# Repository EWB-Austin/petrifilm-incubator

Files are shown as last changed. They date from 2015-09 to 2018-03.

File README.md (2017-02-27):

# The Armadillo v1.0, a Low-cost, Portable, Petrifilm Incubator

The Armadillo v1.0 is a low-cost, portable Petrifilm(TM) Incubator for doing in-country bacterial analysis of water quality for Engineers Without Borders invented and engineered by the Instrumentation Group of [Great Austin Chapter](https://ewbgreateraustin.org/) of [EWB-USA](http://www.ewb-usa.org/).

Watch a 3-minute introductory [video](https://www.youtube.com/watch?v=0SzoYT8wLo0)!

The Armadillo won [1st place](https://ewbgreateraustin.org/2016/11/01/test/) in in the 2016 SCSE Regional Conference in Atlanta poster session contest.
As we like to say, "we beat NASA", with our [poster](https://github.com/EWB-Austin/petrifilm-incubator/blob/master/doc/EWBconferenceposterIncubator_handout_comp.pdf):

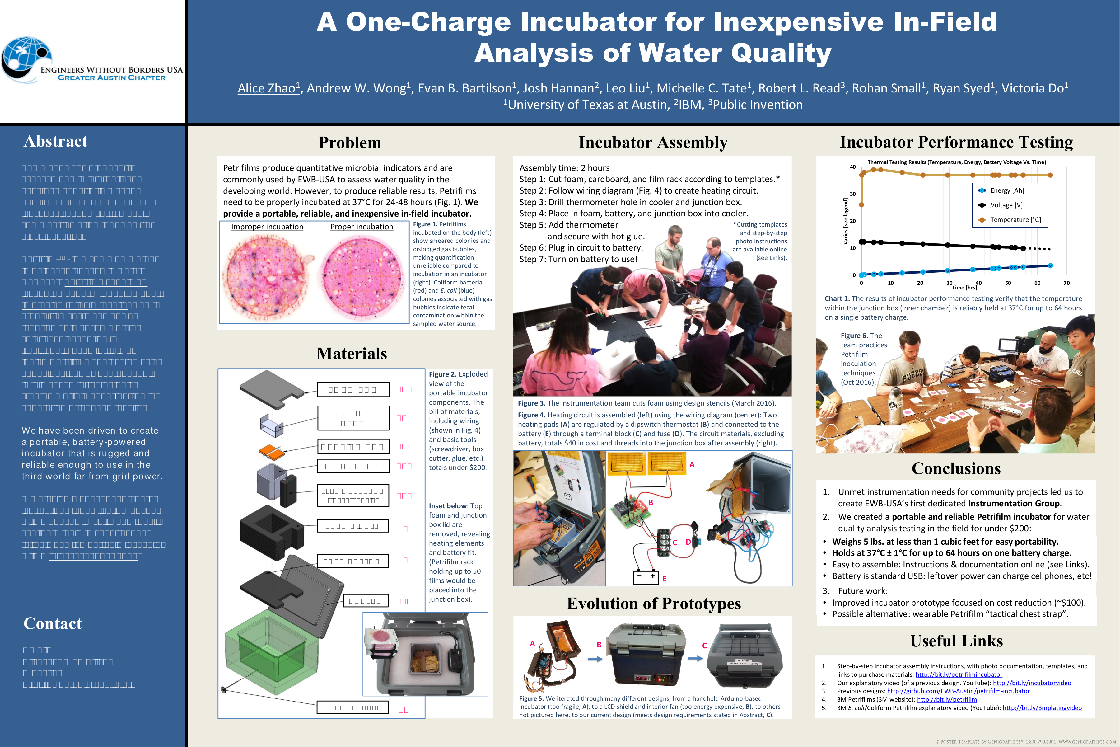
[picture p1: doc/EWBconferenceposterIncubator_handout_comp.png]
poster
.

## Start Here: Documentation

We have a press release in progress which is not yet published.

Our [instructable](http://www.instructables.com/id/Portable-Petrifilm-Incubator-for-Inexpensive-In-Fi/)
gives step-by-step instructions for the construction of the Armadillo for about $160.

For those who prefer printable and sharable PDF, we have prepared a [construction manual](https://github.com/EWB-Austin/petrifilm-incubator/blob/master/doc/ConstructionManual.pdf).

Because the use of the Armadillo requires inoculating Petrifilms, we have prepared an
[inoculation manual](https://github.com/EWB-Austin/petrifilm-incubator/blob/master/doc/PetrifilmInoculation.pdf).

In the [experiments](https://github.com/EWB-Austin/petrifilm-incubator/tree/master/experiments) directory
you will find data from our battery-lifetime experiments.

## Status of the Project

We are:
* Preparing an academic paper with a plan to submit it to [Journal of Humanitarian Engineering](https://www.ewb.org.au/jhe/index.php/jhe).
* Planning some small improvements to create the Armadillo v2.0, such as the inclusion of a screwdriver and
a user manual in the Armadillo itself.
* Promoting the use and construction of the Aramadillo within EWB chapters.

## How You Can Help

We need someone to build an Armadillo!  Although we hope our published materials are self-sufficient,
we are happy to provide personal assistance and help in building your own Armadillo. We want to make
sure that our instruction materials are high-quality.

Please email: <a href="mailto: instrumentationmembers@ewbgreateraustin.org"> instrumentationmembers@ewbgreateraustin.org</a>  or visit our [chapter website](https://ewbgreateraustin.org/) to contact us.

## Older Documents

Our older README is [archived](https://github.com/EWB-Austin/petrifilm-incubator/2016-README.md).

## Contact

[Great Austin Chapter](https://ewbgreateraustin.org/) of [EWB-USA](http://www.ewb-usa.org/).
<a href="mailto: instrumentationmembers@ewbgreateraustin.org"> instrumentationmembers@ewbgreateraustin.org</a>

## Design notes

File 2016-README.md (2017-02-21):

# petrifilm-incubator
A low-cost, portable Petrifilm(TM) Incubator for doing in-country bacterial analysis of water quality for EWB.

Watch a 3-minute introductory [video](https://www.youtube.com/watch?v=0SzoYT8wLo0)!

# Older Materails (These are now mostly obsolete.)

## Problem

Engineers Without Borders does wonderful work providing better-quality water to under-developed communities. Essential
to this is water quality analysis. The 3M Petrifilm(TM) is a widely used way of assessing bacteria load. It requires that
inocultated films be incubated at precise temperatures. Generally, EWB works in communities that have no electrical grid.
The problem then is to reliably incubate the Petrifilm with battery power.

EWB has discoverd that by doing this locally rather than sending the films to a lab, we build trust with the local communities.

An EWB Austin member, Anjan Contractor, led the creation of an initial prototype.  However, it is fragile and undocumented.
This project intends to build a robust, cheap, easy-to-make, easy-to-use, well-documented extension of this prototype.

incubatordiagram

## Commercial Solutions

<p> Eric found the following potential commercial solutions:
[Compact Incubator](http://nelsonjameson.com/Compact-Incubator-p1298.html)  This is $94. We are trying to determine if this can be used with a 12 Volt battery. We may buy one for experimentation.
</p>

<p>
[Bigger Incubators](http://www.darwinchambers.com/Portable-Incubators.html)  These don't have prices listed.
</p>

## Notes from November 14th

After purchasing Compact Incubator mentioned above, we find it completely inadequate to our purposes.

We have, however, made signifcant progress in the design of an improved system.

Our basic approach was to purchase a smaller cooler: [http://www.amazon.com/gp/product/B000IBWI42?psc=1&redirect=true&ref_=oh_aui_detailpage_o03_s00](http://www.amazon.com/gp/product/B000IBWI42?psc=1&redirect=true&ref_=oh_aui_detailpage_o03_s00)
and place our Arduino-based system inside it, with the battery on the outside.

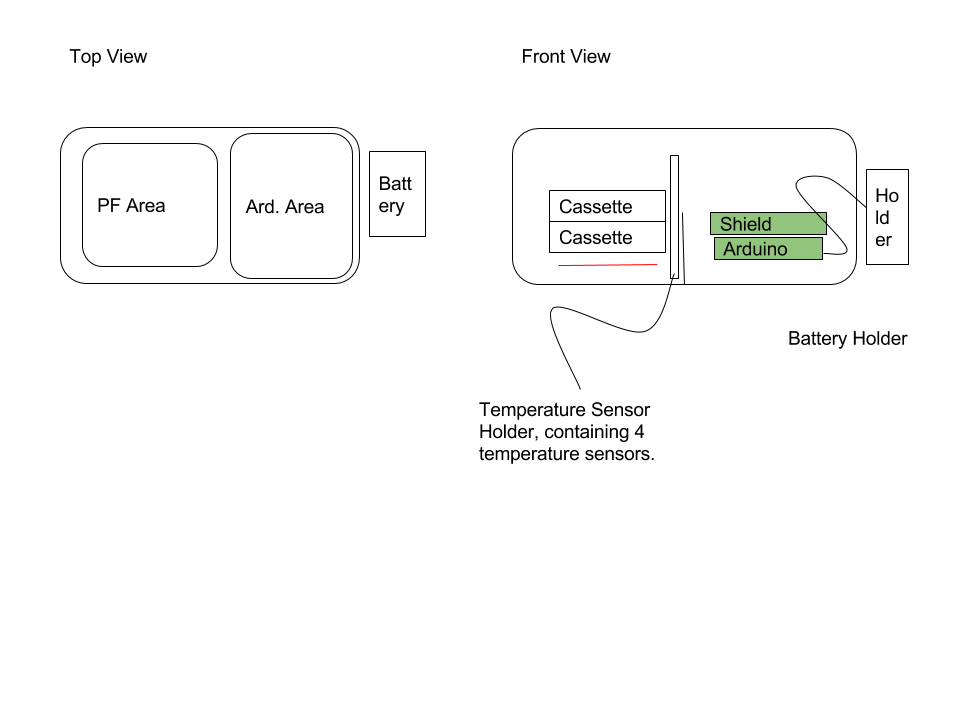
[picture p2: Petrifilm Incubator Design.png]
Image of Yaktocat


## Research Notes

(Thanks to Alice Zhao.)

1-5.
An evaluation of 5 different coliform detection techniques used on-site, including the 3 I talked about in Monday's presentation (Petrifilm, waterworks EZ(which they refer to as just MUG), lacotte multi-tube). They address some of the same issues I brought up, among other useful information.
http://www.ewb-usa.org/files/EWB-USA-TP-104-Fecal-Coliform-Contamination-of-Drinking-Water-an-Evaluation-of-World-Field-Techniques-revc.pdf

6. A 6th method of coliform detection similar to petrifilm but that can be stored at room temperature:
http://www.ewb-usa.org/files/2015/05/AssessmentWaterTestingTechniquesEColi.pdf
Product: http://www.emdmillipore.com/US/en/product/Coli-Count%E2%84%A2-Sampler,MM_NF-MC0010025?bd=1
evaluation of product robustness (for food. full disclaimer I have not read this paper)

7. Colilert is apparently also used by some EWB groups. I thought it was way too expensive when I was initially researching but I may have been wrong. I'll have to do more research on this.

7. A nice blog post of an EWB trip. They used actual petri dishes plates. According to Jen, this is what they use in her workforce when testing for coliform. I don't think this is a top candidate method for us but I like the blog and think we should do something similar for our trip.
http://www.ewbny.org/june_trip_update_part_2_quality_control

8. You asked about "presumative" coliform test and I don't feel like I gave a clear answer. 
Page 2 of this lab manual has a much better explanation.

9. An easy-to-read presentation on water testing in developing countries. Not as informative as it looks at first glance to me, but worth a glance. They seem to advocate using Petrifilm and the human body as an incubator. http://www.ewb-usa.org/files/2015/05/MicrobialTestingOfWater.pdf

10. I was very wrong about the lack of people using Petrifilm for water testing in developed countries. Another advocate of using Petrifilm, among some other techniques:
https://aguainroatan.wordpress.com/2015/07/31/water-testing-in-a-development-context/

Note: here is a different attempt to create that:

http://www.ewb-usa.org/files/2015/05/PortableIncubator.pdf

# Packaging Notes

I now believe it might be both possible and a good idea for us to package the temperature stand into an enclosure that contains the Arduino and the LCD shield.  This would allow the wires to be far better contained and the whole system to be neater. This will really make a big difference in the ruggedness. However, I want to get the EEPROM stuff improved so that we can test the timing.

# Update as of 12/30/2015

I've posted the results of an overnight experiment, in which we used the new EEPROM logging code to record the temperature vs time:
https://github.com/EWB-Austin/petrifilm-incubator/blob/master/TemperatureVsTime1.csv

In summary, it took a long time to warm up, and the battery died after 13 hours.  We really want to stay at 37C for 12 hours on one battery charge, so I consider this a partially successful experiment.

## The Second Prototype

This is our second prototype, based on an Arduino and an LCD shield.  It has now been potentially obsoleted by the third prototype (described below):



# Update as of 3/9/2016

Thanks largely due to the work of Evan Bartilson, we now have a third prototpye, which has currently demonstrated a battery life of 35 hours, and which we expect to acheive our goal of 48 hours.

Below are some photos of our team working and the current incubator.





# Our submission to the Rice NEWT Challenge

We have applied to the [Rice University NEWT Global Water Technology Challenge](http://ricenewt.rice.edu/competition/). We have made a short video, which we will post on April 15th after the competition.  Here is the Abstract we submitted:

## Abstract: Engineers Without Borders (EWB-USA), Austin, Petrifilm Incubator 

Providing potable water to the world requires an ability to tell when water is potable. Our experience has been that to be effective, the means of measuring bacteria and explaining it to people in the developing world must be visible, understandable, quantitative enough to support meaningful comparisons, cheap, and be done completely in the field far away from electrical power grids. Petrifilms(™) provided by 3M corporation are a standard way of accomplishing this. They must be incubated at approximately 37C for 48 hours.  This is traditionally done in the field by keeping the films in plastic bags against the skin of engineers in the field. This is uncomfortable, may not provide the correct temperature, and the films are meant to be kept flat and horizontal during incubation.

In US laboratories, commercial incubators cost hundreds or thousands of dollars. These require 110V power. We are building a portable, battery powered incubator that is rugged and reliable enough to use in the third world. This will allows trustworthy in-the-field analysis and comparison of water sources. Because the analysis is done completely locally and results in visible, comparable films, local people will appreciate and trust the result. Although in the US the growth of a single colony is considered a sign of danger, many of the communities that Engineers Without Borders works with cannot afford this level of quality and must have a quantitative tool that lets them compare water sources and water improvements solutions.

Our first prototype used an Arduino microcontroller in a hand-insulated box. Battery life was 18 hours. The operator changed the batteries before they ran out. This was shown to be effective in a remote community in Peru. However, it was fragile. In a second trip a wire broke and could not be repaired by our staff in the field, highlighting to us the importance of documentation and training.

Our second prototype is completely open-source, described at [GitHub. ](https://github.com/EWB-Austin/petrifilm-incubator) This prototype has developed into a third prototype which has held temperature at 37C for 35 hours. We have hopes of extending battery life to 48 hours with small improvements to this basic design. Our overriding goal is to produce a set of open-source instructions that allows anyone in the world to construct and reliably use the portable petrifilm incubator with modest skill and readily available tools at a total cost of $200.

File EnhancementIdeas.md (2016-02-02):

Here a number of loose enhancement ideas:

* Don't try to run two heat boxes with one Arduino.  Make separate units.
* Try to run everything on 12 volt system, but allow multiple jacks to support parallel battery capabilities.
* Put the Arduino in the heat chamber to take advantage of the waste heat.
* Keep the batteries outside.
* Use and LCD shield to provide better status.
* Provide an audio and visual alarm when the temperature is out of spec for too long.
* 

# Idea: Build the thing into the cap of a thermos bottle.

# Idea: Make it something that essentiall "wraps around" a battery pack.

# Note: I have now created a printed circuit board for this purpose.

I have not yet tested it. It is shared at OSH Park as "Petrifilm Incubator Board" under this profile: https://oshpark.com/profiles/RobertLRead .

# Idea: Make an Arduino Shield Incubator.

This would be a little weird.  We could technically make a Shield for an Arduino. This coult possibly have a projection on a PCB to hold the petrifilms.  Above it we could place our LCD shield. The result would be a very small and elegant system for what we are doing.  We would have to provide insulation in some other manner.

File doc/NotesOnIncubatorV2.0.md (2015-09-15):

# Notes on Incubator V 2.0

I'm assigning the Petrifilm Incubator that we received from Peru the version number 2.0.

## Notes from Conversation with Anjan

The existing incubator control box is set up to drive two incubators. However, we only have one heat-controlled box.
This is why there are so many wires -- one pack of wires is for the second insulated box.

Round battery packs are 12V battery packs.  They drive the Arduinio itself, not the heater.  They are charged using
the aligator clips and the Tenergy charger. They exist to try to keep the Arduino alive through an 18 hour cycle.

An 18 hour cycle is much better for the user, as it allows them a full day away or a full night of sleep before changing
the battery.

These batteries are meant to be connected to the Arduino in parallel to allow a long lifetime.

At present, the connectors that are named the "black" connectors, marked with a piece of tape with the letter "B", 
is broken off.  This needs to be repaird.  These connectors exist to connect the battery packs in parallel to extend
the lifetime of the system.

The blue, 9.8 Amp-hour LiPo batteries are used to drive the heaters.  They may provide 16 hours of heat based on the 
outside temperature.  The green connector with the white female connector is the one to use.  The white connector must
be connected to the red mail connector from the heater box.

When the heater element is on, the green led is on.

The cooper foil was used as a construction material to spread heat evenly within the insulated box.

As far as we know, the petrifilms can be stacked inside the heat-box.  As far as we know, you cannot over-incubate a
petrifilm.  This needs to be tested.

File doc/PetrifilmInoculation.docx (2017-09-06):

Inoculation Materials:

- Individually wrapped 1mL sterile transfer pipettes
- 5mL (or larger) sterile glass sample vials
- Enough 3M Petrifilm plates for all water samples
- 3M Petrifilm spreader
- A sharp-tipped permanent marker

Inoculating and incubating Petrifims is easy, but a little practice helps. Please read over these instructions before you begin. You may want to practice an inoculation and your sample handling process in a “dry run” before you use up your Petrifilms.

1. Obtain sterile pipettes with volume measurements on the sides as well as small (~5mL), sterile sample vials for samples.
2. Use sterile pipettes to take samples from different locations and store in the containers. Ideally, you should collect the samples and perform the inoculation and begin incubation within one hour, or as soon as possible, but not more than 24 hours. Store the samples in a room temperature environment away from sunlight.
3. You may find it useful to label each vial/jar with a Sharpie. Carefully record the date, time, and place of sample collection and name of the person sampling to associate with the mark on the vial. Because that is too much to write on a vial or a Petrifilm, you will want to to associate each sample with a short, abbreviated codename like “A1” or “TUR-3”.
4. When you are ready for inoculation, place the 3M petrifilm plate on a level surface. Use a permanent marker to label the corner of the petrifilm with the codename of the sample that it will be used for.
5. Shake the sample gently to make sure the bacteria are not at the top or bottom of the sample. With a sterile pipette, draw 1mL of samples from the chosen sample vial.
6. Lift the clear top film and with the pipette perpendicular to the inoculation area slowly dispense 1mL of samples onto the center of the bottom film.
7. Roll the top film down onto the sample to prevent trapping air bubbles.
8. Place the 3M Petrifilm spreader with the flat side down on the center of the 3M Petrifillm plate. Press gently on the center of the 3M Petrifilm spreader to distribute the sample evenly. Do not slide the 3M Petrifilm Spreader across the film.
9. Remove the 3M Petrifilm spreader and leave the 3M Petrifilm plate undisturbed for at least one minute to permit the gel to form.
10. Your samples are ready to be placed in the Armadillo for incubation. Be sure to handle the Petrifilms carefully when transferring to the Armadillo.
11. You are allowed to stack as many 20 petrifilms together, but not more than that. The Armadillo allows you to incubate 40 petrifilms with a small cardboard stand for a second stack of 20.
12. When the 48 hours is up, IMMEDIATELY take the petrifilms out and photograph them clearly, including the sample label in the photograph. Petrifilms change their appearance slowly after incubation, so it is important to take photos immediately.
13. Once you safely have photos, we recommend you dispose of the Petrifilms as they are a slight biohazard.

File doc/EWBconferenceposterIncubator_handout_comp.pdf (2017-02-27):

Assembly time: 2 hours
Step 1: Cut foam, cardboard, and film rack according to templates.*
Step 2: Follow wiring diagram (Fig. 4) to create heating circuit.
Step 3: Drill thermometer hole in cooler and junction box.
Step 4: Place in foam, battery, and junction box into cooler.
Step 5: Add thermometer
and secure with hot glue.
Step 6: Plug in circuit to battery.
Step 7: Turn on battery to use!

# A One⁻Charge Incubator for Inexpensive In⁻Field

# Analysis of Water Quality

## Alice Zhao¹

## , Andrew W. Wong¹ , Evan B. Bartilson

1

## , Josh Hannan

2

## , Leo Liu

1

## , Michelle C. Tate

1

## , Robert L. Read

3

## , Rohan Small

1

## , Ryan Syed

1

## , Victoria Do

1
1University of Texas at Austin,

2
IBM,

## 3Public Invention

## Problem

## Materials

## Conclusions

Incubator Assembly | Incubator Performance Testing

## Useful Links

Figure 3. The instrumentation team cuts foam using design stencils (March 2016).

## Abstract

## Contact

Email:
alicezhao@gmail.com
Website:
http://ewbgreateraustin.org

The means of water quality assessment in international development efforts must be devoid of language dependence, inexpensive, and carried out in communities often far away from electrical grids.

Petrifilm⁽TM) is a common method to detect pathogens in water. However, Petrifilms should be incubated at 37°C for 24-48 hours to provide reliable results. Due to prohibitive costs and power requirements of commercial solutions, incubation is
traditionally done in-field by taping Petrifilms against the skins of engineers. However, not only is this uncomfortable, it also creates multiple opportunities for generating erroneous results.

We have been driven to create a portable, battery-powered incubator that is rugged and reliable enough to use in the third world far from grid power.

We provide a set of open-source instructions that will allow anyone with modest DIY skills and readily available tools to construct and reliably use the portable incubator with a total cost under $200.

1. Unmet instrumentation needs for community projects led us to create EWB-USA’s first dedicated Instrumentation Group.
2. We created a portable and reliable Petrifilm incubator for water quality analysis testing in the field for under $200:
3. Future work:

Petrifilms produce quantitative microbial indicators and are commonly used by EWB-USA to assess water quality in the developing world. However, to produce reliable results, Petrifilms need to be properly incubated at 37°C for 24-48 hours (Fig. 1). We provide a portable, reliable, and inexpensive in-field incubator.

## Evolution of Prototypes

Figure 4. Heating circuit is assembled (left) using the wiring diagram (center): Two heating pads (A) are regulated by a dipswitch thermostat (B) and connected to the battery (E) through a terminal block (C) and fuse (D). The circuit materials, excluding battery, totals $40 in cost and threads into the junction box after assembly (right).

FOAM TOP

PETRIFILM
RACK

HEATING PAD

JUNCTION BOX

132Wh BATTERY
(rechargeable)

FOAM MIDDLE

FOAM BOTTOM

COOLER

THERMOMETER

$15

$3

$8

$15

$65

$30

$6

Improper incubation | Proper incubation | Figure 1. Petrifilms incubated on the body (left) show smeared colonies and dislodged gas bubbles, making quantification unreliable compared to incubation in an incubator (right). Coliform bacteria (red) and E. coli (blue) colonies associated with gas bubbles indicate fecal contamination within the sampled water source.
*Cutting templates
and step-by-step
photo instructions
are available online
(see Links).

Figure 2. Exploded
view of the
portable incubator
components. The
bill of materials,
including wiring
(shown in Fig. 4)
and basic tools
(screwdriver, box
cutter, glue, etc.)
totals under $200.

Inset below: Top
foam and junction
box lid are
removed, revealing
heating elements
and battery fit.
(Petrifilm rack
holding up to 50
films would be
placed into the
junction box).

A

B

C D

E

- Weighs 5 lbs. at less than 1 cubic feet for easy portability.
- Holds at 37°C ± 1°C for up to 64 hours on one battery charge.
- Easy to assemble: Instructions & documentation online (see Links).
- Battery is standard USB: leftover power can charge cellphones, etc!

Chart 1. The results of incubator performance testing verify that the temperature within the junction box (inner chamber) is reliably held at 37°C for up to 64 hours on a single battery charge.

Figure 6. The
team practices
Petrifilm
inoculation
techniques
(Oct 2016).
1. Step-by-step incubator assembly instructions, with photo documentation, templates, and links to purchase materials: http://bit.ly/petrifilmincubator
2. Our explanatory video (of a previous design, YouTube): http://bit.ly/incubatorvideo
3. Previous designs: http://github.com/EWB-Austin/petrifilm-incubator
4. 3M Petrifilms (3M website): http://bit.ly/petrifilm
5. 3M E. coli/Coliform Petrifilm explanatory video (YouTube): http://bit.ly/3mplatingvideo

Figure 5. We iterated through many different designs, from a handheld Arduino-based incubator (too fragile, A), to a LCD shield and interior fan (too energy expensive, B), to others not pictured here, to our current design (meets design requirements stated in Abstract, C).

A | B | C
- Improved incubator prototype focused on cost reduction (~$100).
- Possible alternative: wearable Petrifilm “tactical chest strap”.

0

10

20

30

40

0 | 10 | 20 | 30 | 40 | 50 | 60 | 70 Varies [see legend]

Time [hrs]

Thermal Testing Results (Temperature, Energy, Battery Voltage Vs. Time)

Energy [Ah]

Voltage [V] Temperature [°C]

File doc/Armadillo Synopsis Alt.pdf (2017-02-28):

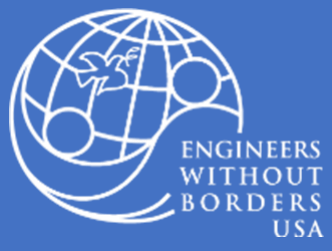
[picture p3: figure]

https://ewbgreateraustin.org/https://github.com/EWB-Austin/petrifilm-incubator

What is the Armadillo?

Armadillo is an open source device that enables on-site quantification of waterborne E.coli and coliform bacteria. The device utilizes inexpensive bacterial indicating plates and is capable of incubating up to forty on a single battery charge. Once inoculated with small samples of water these bacterial indicating plates are exposed to 37°C for a period of 48 hours inside of the Armadillo after which they display the presence and quantity of potentially harmful bacteria.

Why is the Armadillo needed?

Water quality improvement projects in developing countries often require on-site analysis and languageindependent data visualization. Currently, bacterial indicating plates are incubated by taping them against an engineer’s skin for the duration of the incubation which proved to be an irritating and error-prone process. This analysis may also be carried out by external labs, a time expensive process that generates data which is hard to use persuasively with community members. Armadillo offers a simple, low-cost solution.

How difficult is Armadillo to make?

Armadillo costs less than $200 and can be assembled in less than 2 hours with parts readily available at a hardware store and/or Amazon. Instructions can be found here: instructables.com/id/Portable-Petrifilm-Incubator-for-Inexpensive-In-Fi/ (http://www.instructables.com/id/Portable-Petrifilm-Incubator-for-Inexpensive-In-Fi/)

Specifications

- Allows for 65 hours of incubation at 37±1°C†
- Material cost under $150
- Only 2 hours of assembly time required

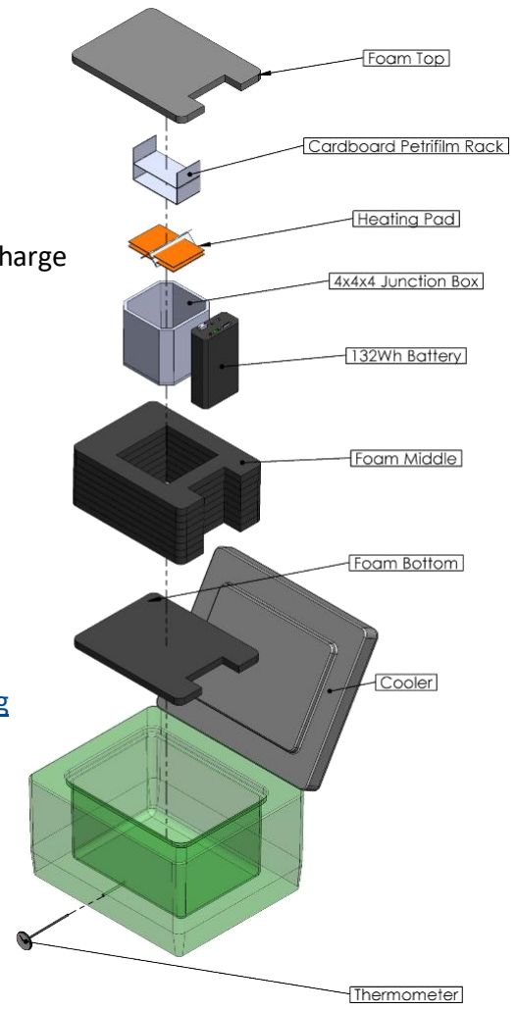
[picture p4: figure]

- Capable of incubating 40 indicating plates per battery charge
- External temperature display
- Weighs only 7 pounds

†
At external temperatures below 22°C run time may be reduced

Who created Armadillo?

A collection of students and professionals working at EWB-USA -Greater Austin Chapter.

Where can I find out more?

Contact us at instrumentation-members@ewbgreateraustin.org with any questions, comments, or concerns.

## “Armadillo 1.0”

## A Low-Cost Off-Grid Water Pathogen Testing Device

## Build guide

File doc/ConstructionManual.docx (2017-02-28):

Construction of Armadillo V1.0: A Low-Cost Incubator for Off-Grid Water Quality Analysis

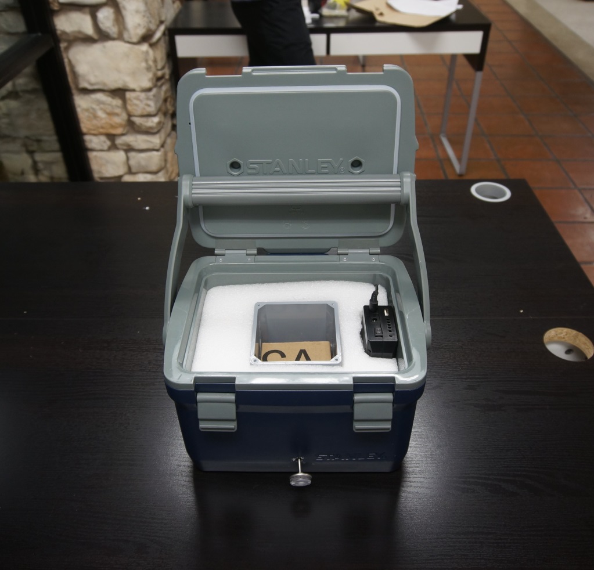
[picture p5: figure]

This document details the construction of Armadillo V1.0, a battery-powered 3M Petrifilm™ incubator. Once assembled, the incubator can be used to perform visual, on-site bacterial analysis of water samples. This device was developed in 2016 by the Greater Austin Chapter of Engineers Without Borders USA.

Contact us at instrumentation@ewbgreateraustin.org

Table of Contents

# Motivation

Lack of access to clean water is one of the greatest challenges of the 21st century. Water quality improvement projects require accurate identification of contaminated water, and such efforts in third world countries often require rapid on-site analysis and language-independent data visualization. While water samples can sometimes be sent to third-party laboratories that perform analytical services, this method is expensive, time-consuming, and limited in availability. Alternatively, 3M™ Petrifilm™ E. coli/Coliform Count Plates are a highly effective method for on-site detection of harmful bacteria in water. The plates are cost-effective and convenient, and provide quantitative visually striking results that are easy to communicate to local communities.

While Petrifilm plates can provide water quality engineers in the field with powerful visual analysis at a low cost, the plates require a 48-hour incubation period at 37°C. Due to the high cost and energy requirements of commercial incubators, many workers currently accomplish this by fastening the plates to their bodies, a method which is inconvenient, inconsistent, and error-prone. Armadillo offers a simple, low-cost incubation solution.

The incubator described here is easy to assemble, easy to operate, low-cost, battery-powered, rugged, and reliable. In a 22-25°C environment, Armadillo can incubate 40+ Petrifilm plates beyond the 48 hours required to complete analysis.

# Audience

The primary audience for this manual is anyone interested in detecting the presence of potentially pathogenic bacteria in water. Construction of the incubator requires only basic familiarity with hand tools and the ability to connect simple electrical components. A secondary audience may be engineering students interesting in learning fabrication skills and those who require incubation for other purposes.

# Required Materials

The incubator is constructed out of a housing container, insulation, resistive heating pads, a thermostat, a battery, and basic cardboard Petrifilm Count Plate shelves. Below, we include a list of the materials used in the construction of this device, with links to potential suppliers. All materials were purchased from Amazon, with the exception of the Adafruit heating pad sources from Adafruit, and the foam insulation sourced from Home Depot. In addition to these materials, please print the paper templates found in Appendix A. These will be used to cut the foam and cardboard to the appropriate size.

Item | Link | Cost | Qty | Cost EXT
Insulated Container | Stanley Adventure Cooler (https://www.amazon.com/gp/product/B00JYFGY0C/ref=ox_sc_act_title_7?ie=UTF8&psc=1&smid=ATVPDKIKX0DER) | $ 29.97 | 1 | $ 29.97
Heating Pad | Adafruit Heating Pad: 10cm x 5cm (https://www.adafruit.com/products/1481) | $ 3.95 | 2 | $ 7.90
Thermostat | DROK 090097 Thermostat (https://www.amazon.com/gp/product/B00GFF5YXM/ref=ox_sc_act_title_7?ie=UTF8&psc=1&smid=AFHAE9RJVUMB) | $ 10.10 | 1 | $ 10.10
Battery | TalentCell Rechargeable 12V/11000mAh (http://www.amazon.com/TalentCell-Rechargeable-11000mAh-14500mAh-26400mAh/dp/B016BJCRUO) | $ 64.99 | 1 | $ 64.99
Foam | R-4 Insulated Foam: 0.75 in. x 4 ft. x 8 ft. (http://www.homedepot.com/p/Owens-Corning-FOAMULAR-3-4-in-x-4-ft-x-8-ft-R-4-Tongue-and-Groove-Insulating-Sheathing-37L/100320340) | $ 15.56 | 1 | $ 15.56
Junction box | Junction Box Enclosure (http://www.amazon.com/Waterproof-Plastic-Sealed-Junction-Enclosure/dp/B00RE6HWEA) | $ 10.06 | 1 | $ 10.06
Terminal block | 4 Position Terminal Strip (http://www.amazon.com/Position-Covered-Screw-Terminal-Strip/dp/B008DS266M) | $ 4.97 | 1 | $ 4.97
Speaker Wire | 16-Gauge Speaker Cable: 25 ft. (https://www.amazon.com/dp/B00NSGCVWI) | $ 5.36 | 1 | $ 5.36
Thermometer | Cooper-Atkins Pocket Thermometer (http://www.amazon.com/Cooper-Atkins-1246-02C-1-Thermometer-Adjustment-Temperature/dp/B009ZZ3R3S) | $ 5.90 | 1 | $ 5.90
Fuse | Iztoss Waterproof Fuses (http://www.amazon.com/Waterproof-Blade-Holder-Fuses-10pcs/dp/B01531YFYW) | $ 3.99 | 1 | $ 3.99
Crimp kit | Neiko 50413A Crimp Kit (http://www.amazon.com/50413A-Terminal-Connection-Crimpers-Stripper/dp/B000K7GRCI) | $ 12.40 | 1 | $ 12.40
| | | SUM: | $ 171.20

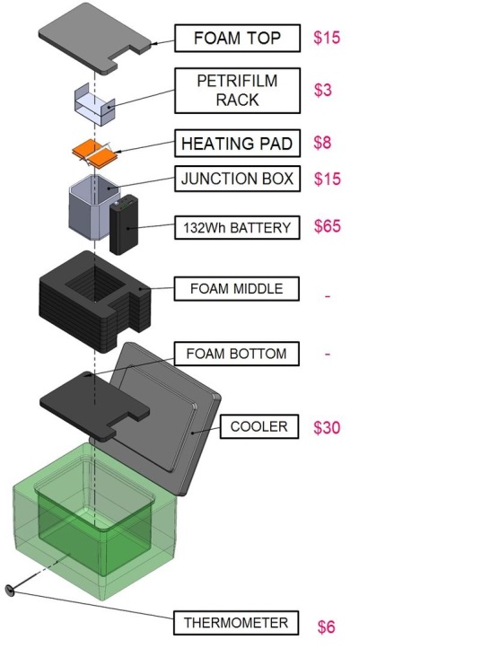
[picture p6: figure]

# Construction of Armadillo

## Cutting of Insulation

The first step in constructing Armadillo is to cut R-4 foam into the appropriate shapes. Using the templates provided, cut the foam into one top layer, one bottom layer, and nine middle layers. If using a foam thickness other than ¾ inch, adjust the number of middle layers to completely fill the housing’s interior.

Figure 1: The foam bottom layer.

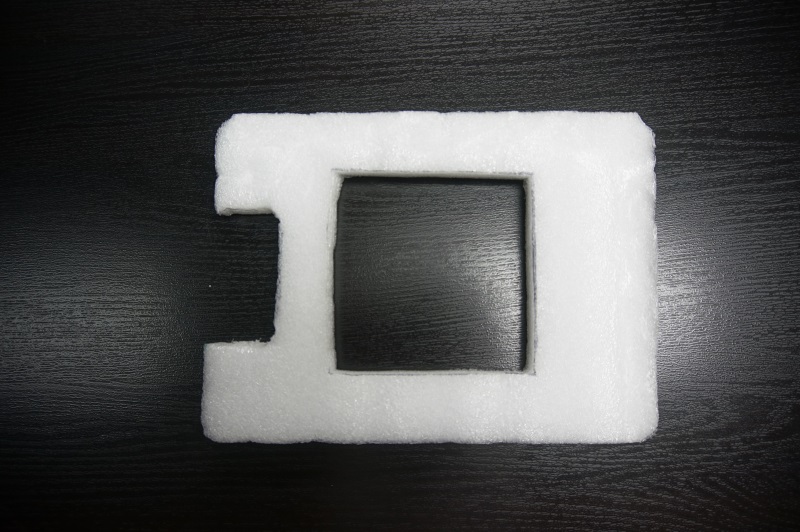
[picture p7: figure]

Figure 2: One of the nine foam middle layers.

Note: For best performance, we recommend use of closed cell foam with a high R-value (capacity of a material to resist heat flow).

## Cutting of the Cardboard

For this prototype, inner chamber components are designed out of cardboard. Use the provided Petrifilm Count Plate Shelf Template to cut an appropriate sized rectangle of cardboard, and crease the rectangle at the designated location using a sharp edge. This shelf can hold up to 20 Petrifilm Count Plates. Create a second shelf on top of the first if you wish to incubate more than 20 plates.

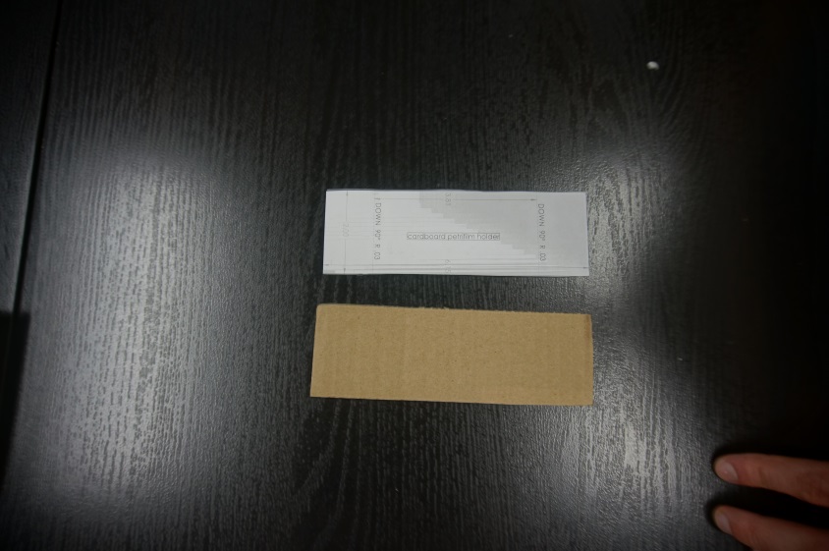
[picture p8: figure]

Figure 3: The Petrifilm Count Plate Shelf Template.

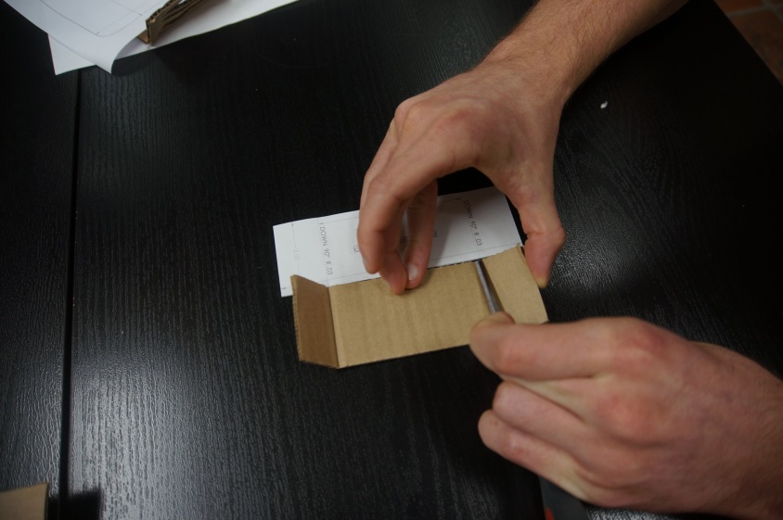
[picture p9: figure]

Figure 4: Creasing the cardboard into the shelf.

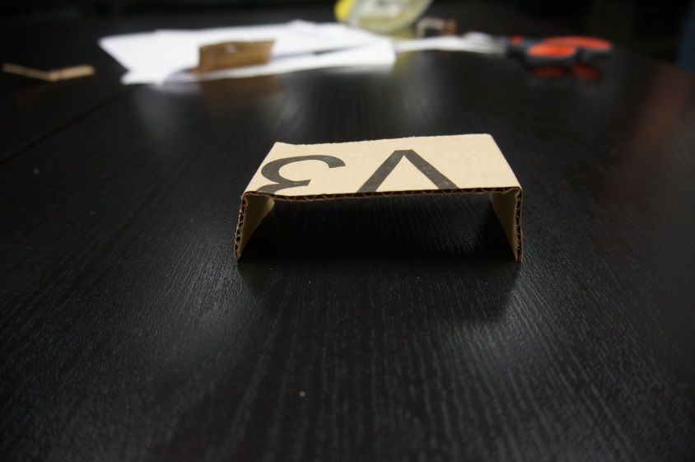
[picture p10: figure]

Figure 5: The completed Petrifilm Count Plate Shelf.

Next, we will be creating the heating pad spacer. The spacer suspends the heating pads to provide effective convection within the inner chamber in which Petrifilm Count Plates are incubated. Cut out a cardboard rectangle using the Heating Pad Spacer Template provided. Cut four slits into the rectangle as shown below, and fold the spacer in half. Finally, cut out a small divot in the base of the spacer. The thermocouple will be mounted here in a later step.

Figure 6: The heating pad spacer fully assembled.

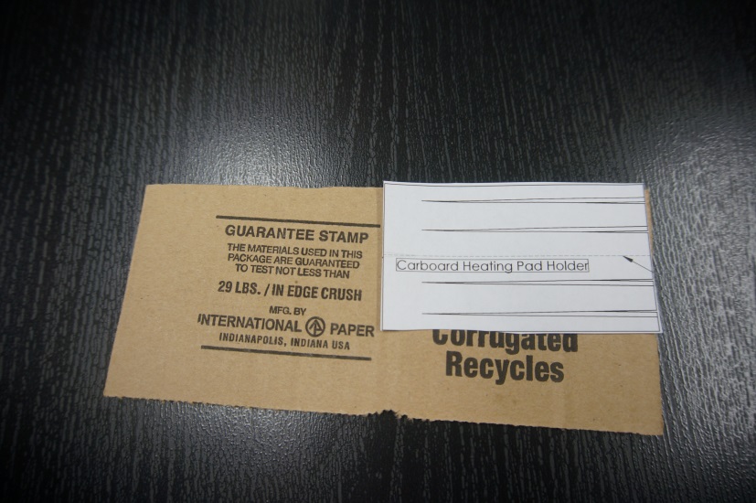
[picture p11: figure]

Figure 7: The Heating Pad Spacer Template.

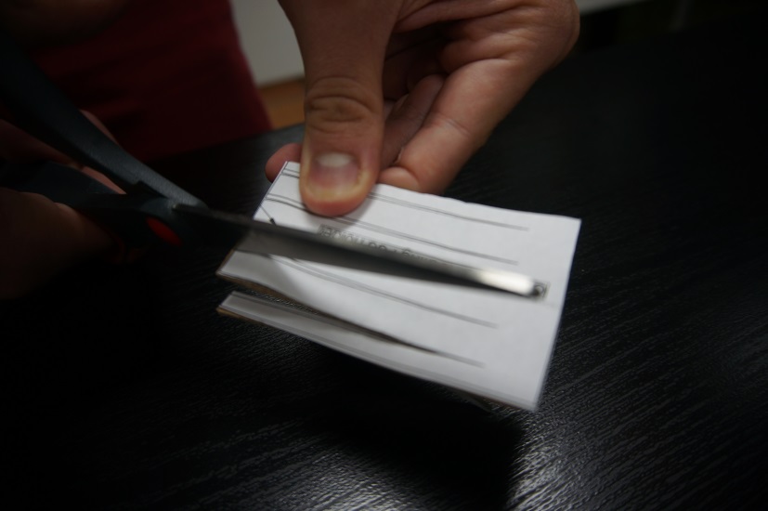
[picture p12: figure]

Figure 8: Cutting the heating pad spacer.

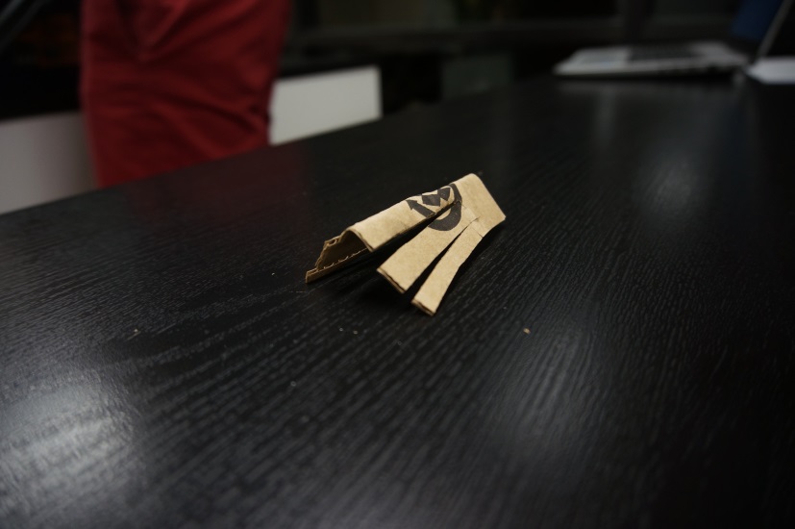
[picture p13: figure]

Figure 9: After cutting out the template, fold the spacer in half at the midpoint.

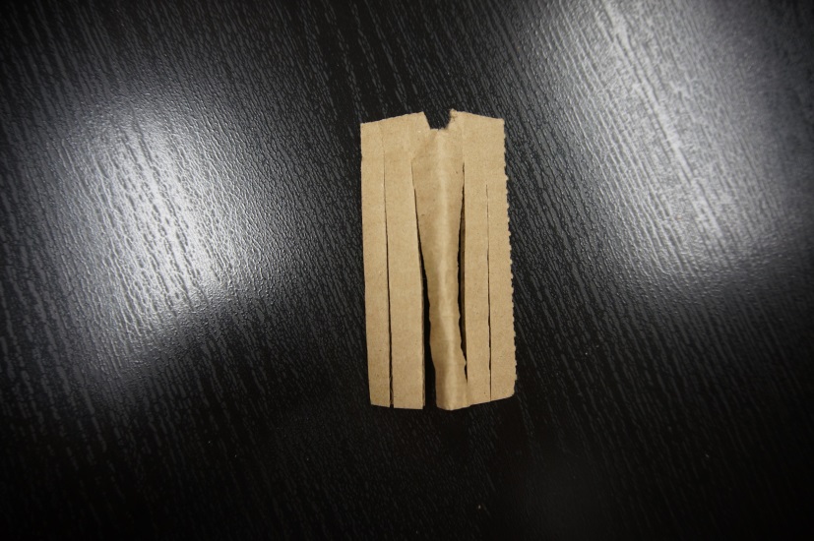
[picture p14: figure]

Figure 10: A top-down shot of the heating pad spacer showing a notch at the top where the thermocouple will rest.

## Drilling the Thermometer Port into the Inner Chamber

Next, we must drill through the outer cooler into the inner chamber. This is done in one step to ensure that the wholes align appropriately, but with careful measurement, these holes may be drilled individually. Use a 5/32” drill bit to create a centered hole located 0.57” above the cooler’s base. If you are using our recommended cooler, use the provided template as shown in Figure 11 to simplify the aligning process.

Prior to drilling, the inner chamber must be firmly situated in its operative position: Lay the bottom layer of foam down in the cooler, and place the inner chamber on top of it. Make sure the inner chamber is snug and centered in the cooler by adding in a middle layer of foam. Once the inner chamber is in position, continue drilling the port into the inner chamber. Once the pilot hole has been drilled, remove the inner chamber, and enlarge the hole to 3/8”. At this point, the thermometer should be able to reach into the chamber.

Figure 11: The thermometer port template.

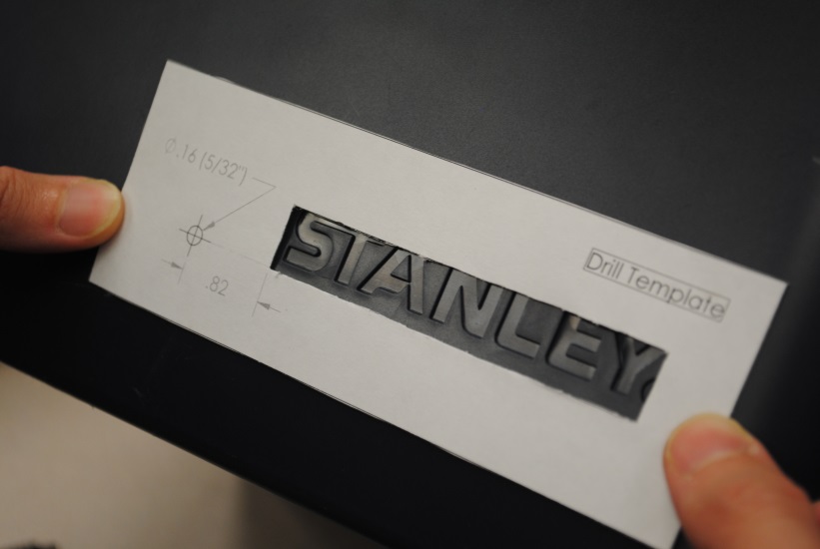
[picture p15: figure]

Figure 12: Aligning the drill template.

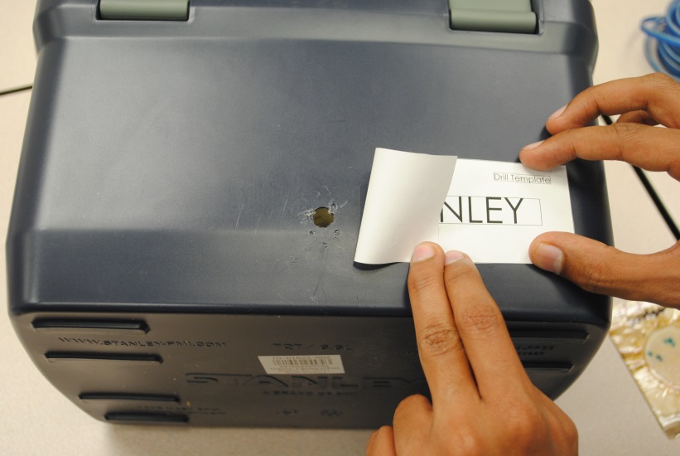
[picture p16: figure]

Figure 13: The completed pilot hole.

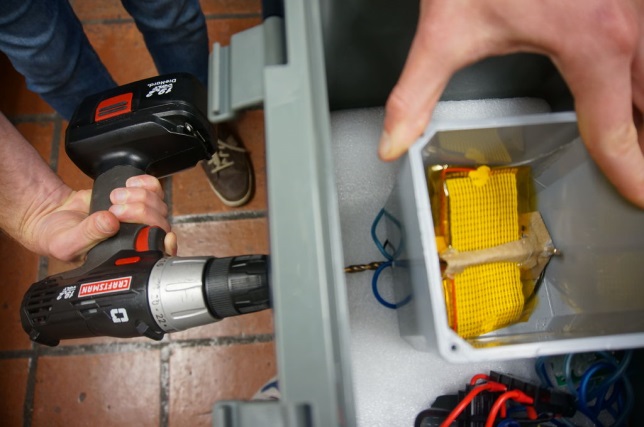
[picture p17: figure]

Figure 14: Continuing the port into the centered inner chamber.

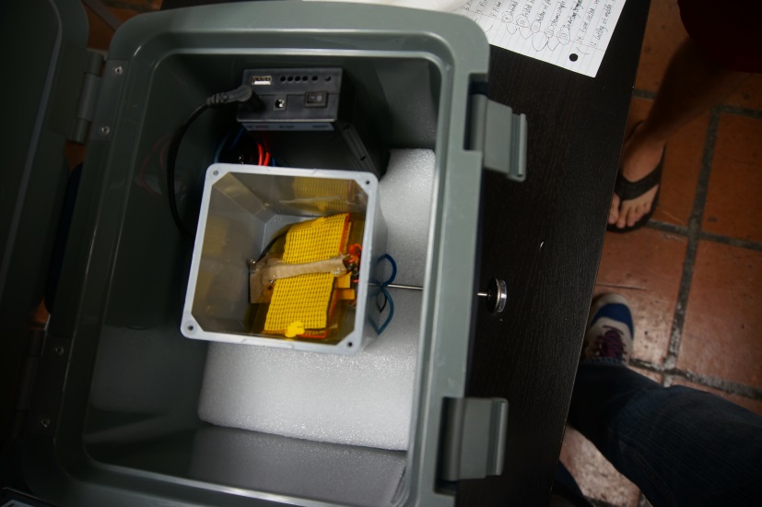
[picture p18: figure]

Figure 15: The thermometer should reach into the inner chamber from outside the cooler.

## Wiring the Electrical Heating System

Armadillo is kept at a constant 37°C by a thermostat controlling two resistive heating pads. A three-position terminal block connects these components to the rechargeable battery through a fuse.

Begin by setting the thermostat to 37°C. This is accomplished by setting position 2 of the red DIP switch on the thermostat to the ON (up) position. All other positions should be set to OFF (down). Next, strip one end of the 5.52 mm male cable to expose positive and negative leads (see Figure 17). Connect each of these exposed leads to fork connectors, and connect the wires to terminals 1 and 2 of the block. Then wire the switch to positions 1 and 3 of the block. Finally, wire the thermostat to the terminal block, as shown in Figure 17.

The heating pads will need to be connected to the thermostat by wires that are 1 foot in length. First, connect the two heating pads in series. Then, connect the one foot wires to the pads, and feed the leads out of the thermometer port so the pads rest in the inner chamber (Figure 18). Connect these leads to the thermostat.

Finally, connect the thermocouple to the thermostat, and feed the sensor into the inner chamber.

Figure 16: An electrical diagram depicting the heating system.

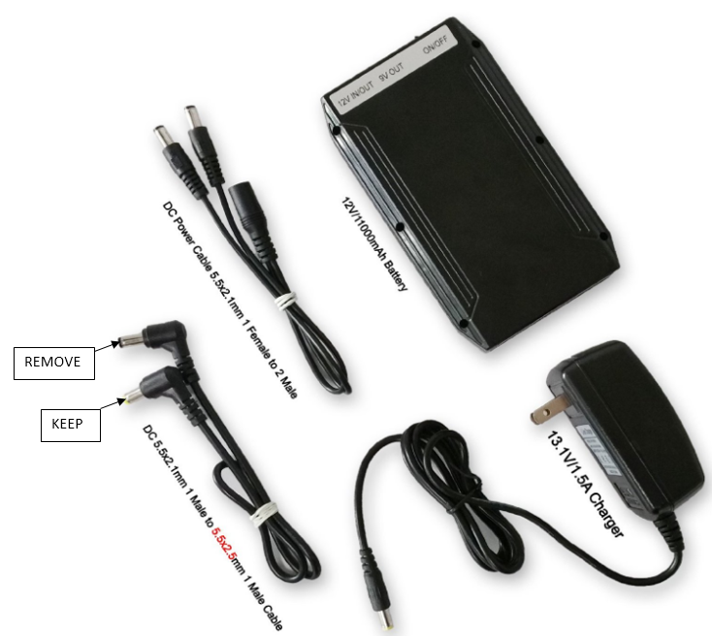
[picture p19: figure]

Figure 17: Remove one of the male connectors from the 5.52 mm cable to allow for an interface with the battery.

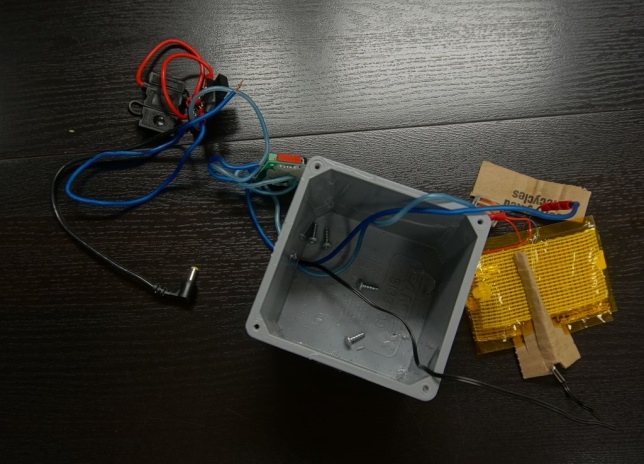
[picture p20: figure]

Figure 18: Feeding the heating pad leads out of the inner chamber, and connecting them to the thermostat.

## Assembling the Complete Heating Unit

In order to ensure efficient distribution of heat, the heating pads must be mounted in the previously constructed heating pad spacer. Slide each of the heating pads into a respective slot, and use a hot glue gun to ensure they are firmly mounted. Place the thermocouple in its respective notch, and mount it in place with hot glue. Finally, place the heating pads in the bottom of the inner chamber.

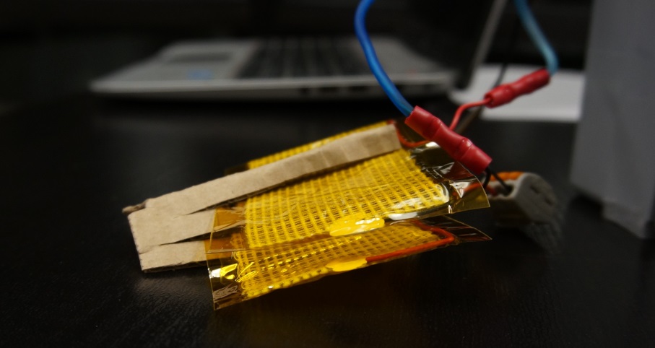
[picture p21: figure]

Figure 19: The heating pads correctly assembled into the heating pad spacer.

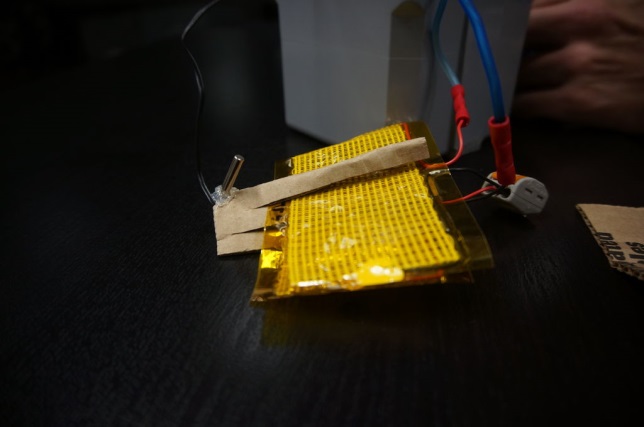
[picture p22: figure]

Figure 20: The heating pad assembly after the thermocouple has been glued in place.

Figure 21: The heating pads are held in the spacer and resting at the bottom of the inner chamber.

## Trimming Foam Insulation to the Appropriate Size

Now that the electrical system has been completed, the foam insulation must be modified to accommodate the thermostat. Use the modified middle foam template to trim one of the insulation pieces as shown. Place the fuse, thermostat, and terminal block on top of the bottom layer of foam. Lay the modified middle layer on top of the bottom layer, position the electrical components in the modified corner. Place a standard middle layer on top of the modified layer, and if any components protrude into this layer, trim the foam as necessary.

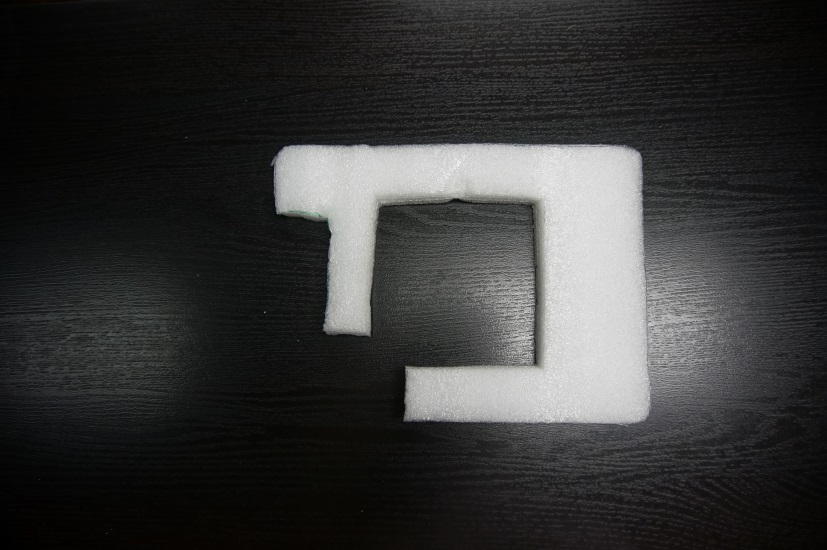
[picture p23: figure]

Figure 22: The modified middle layer of foam.

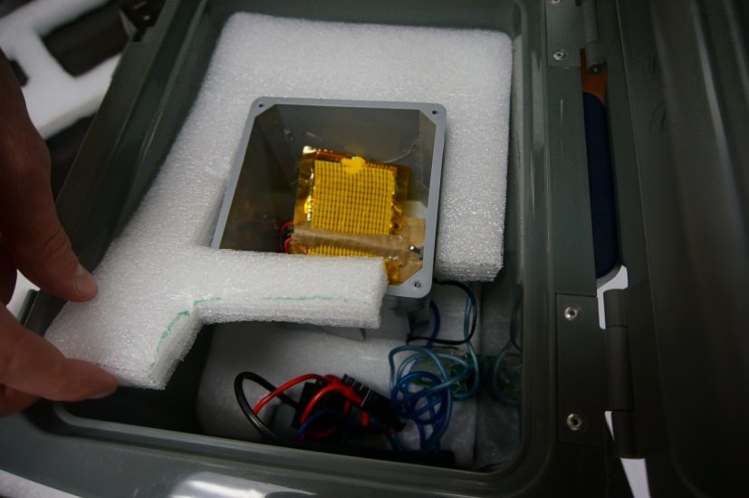
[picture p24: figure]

Figure 23: Ensuring the components are accommodated by the foam modification.

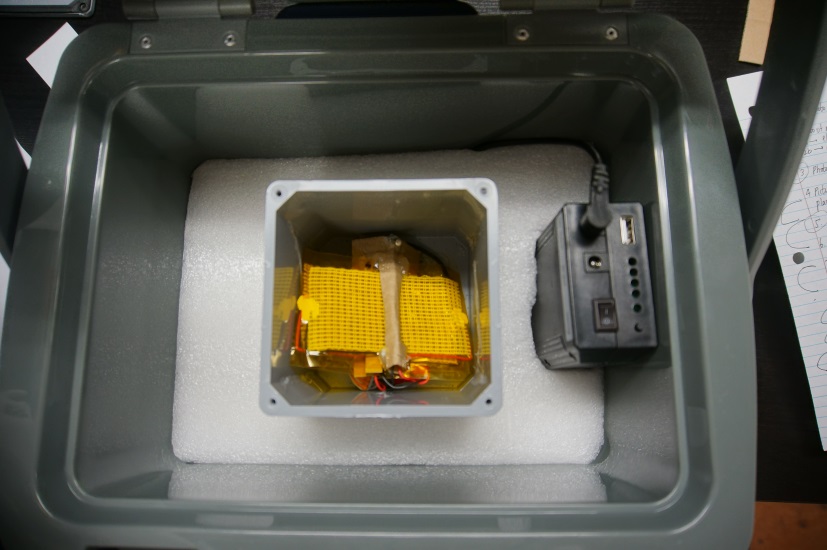
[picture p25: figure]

Figure 24: The next layer of foam should fit on top with no protrusions.

## Mounting the Thermometer

IMPORTANT: After this step, the inner chamber will be permanently mounted in the incubator. Ensure the heating pads and thermocouple are properly inserted in the system.

Now, the thermometer must be firmly mounted in the system. Remove all foam from the cooler except for the bottom layer, and place the inner chamber on top of it. Use a middle layer of foam to ensure the inner chamber is centered in the cooler. Slide the thermometer into the system, ensuring it reaches inside the inner chamber. Apply hot glue around the probes circumference, and fully insert it into the thermometer port. Hold the thermometer in place until the glue sets. After it is mounted in place, apply hot glue around the thermometer port from the inside of the cooler. It is important to ensure a good seal is formed, as this allows the incubator to operate more effectively.

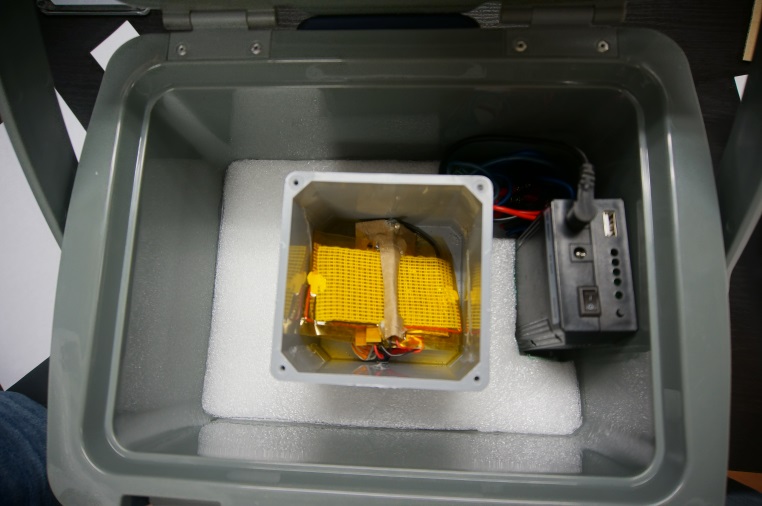
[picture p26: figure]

Figure 25: The inner chamber and electrical system centered in the cooler.

Figure 26: The thermometer should fully insert into the inner chamber.

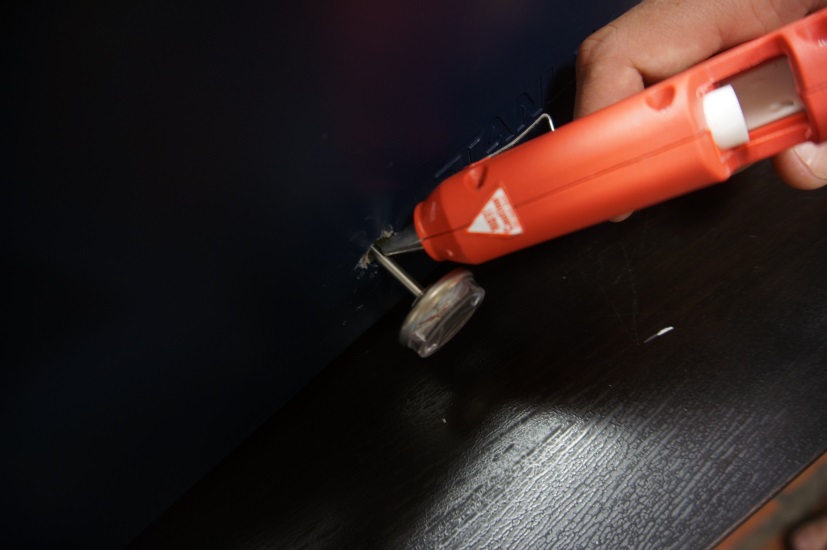
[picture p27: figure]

Figure 27: Completely fill the port with hot glue before completely inserting the thermometer.

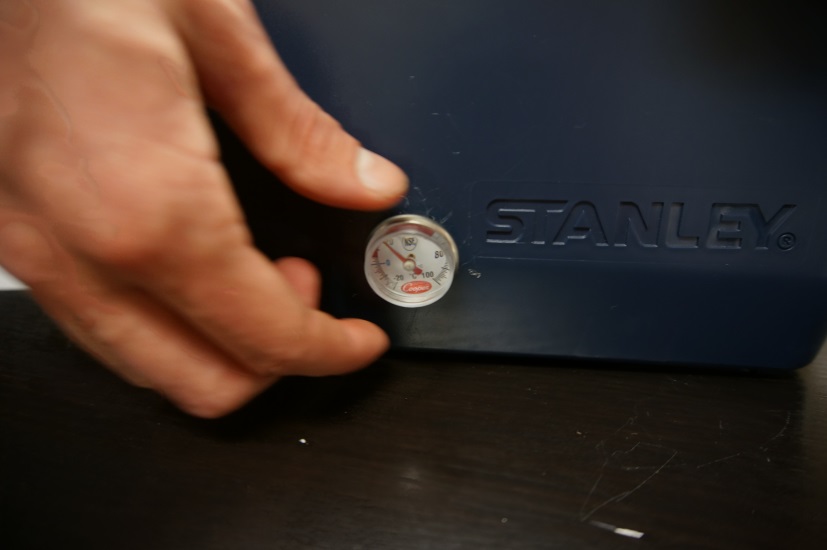
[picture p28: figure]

Figure 28: Ensure the thermometer is firmly mounted in place.

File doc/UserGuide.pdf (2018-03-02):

USER GUIDE

With our instructions, constructing the Armadillo Portable incubator is a fairly simple process and should take 4-5 hours and around $200 to complete. All the required materials are readily available. Constructing the incubator involves wiring a simple circuit with the thermostat and resistive heating pads, cutting the foam and cardboard to the right sizes, drilling holes in the cooler and inner chamber, and packing all the parts inside the cooler. You can find detailed assembly instructions with resources for how to obtain materials in our instructable.

Pre-operating instructions
The specified battery pack fully charges in 24 hours. To use the Armadillo in-country away from grid based AC power, simply charge the battery pack ahead of time in a place where you have power. If multiple 48-hours incubations are required, you may transport spare batteries or find a way to charge the battery in-country.

Sample-handling
It is critically important to collect and handle samples correctly before incubation. If it is not possible to directly inoculate samples from source onto the Petrifilm Count Plates, water samples should be collected in sterile containers and transported out of direct sunlight for a minimal amount of time. Each
E. coli Petrifilm requires 1 milliliter of water. A convenient container for sample collection is small 5 ml vials.
Vials should be clearly numbered by a permanent marker with the source, condition, and time of sample collection should be recorded. Furthermore, samples should be kept cool and dark, and not exposed to bright sunlight or excessive heat. Finally, we recommend inoculating samples within 24 hours of collection.
We find it convenient to write identifying information for each sample with a permanent marker directly on the top of each petrifilm (outside of the circle where the growth medium is found) as it is inoculated.

Inoculation
Operators should practice inoculation and incubation with the Armadillo at home to be confident of procedures in the less comfortable environment in the field.

Inoculation Materials:
- Individually wrapped 1mL sterile transfer pipettes, (http://www.globescientific.com/transfer-pipets-c-32.html)
- 5mL (or larger) sterile glass sample vials,
- Enough 3M Petrifilm plates for all water samples,
- 3M Petrifilm spreader, and
- A sharp-tipped permanent marker.

Inoculating and incubating Petrifims is easy, but a little practice helps. Please read over these instructions before you begin. You may want to practice an inoculation and your sample handling process in a “dry run” before you use up your Petrifilms.
1. Obtain sterile pipettes with volume measurements on the sides as well as small (~5mL), sterile sample vials for samples.
2. Use sterile pipettes to take samples from different locations and store in the containers. Ideally, you should collect the samples and perform the inoculation and begin incubation within one hour, or as soon as possible, but not more than 24 hours. Store the samples in a room temperature environment away from sunlight.
3. You may find it useful to label each vial/jar with a Sharpie. Carefully record the date, time, and place of sample collection and name of the person sampling to associate with the mark on the vial. Because that is too much to write on a vial or a Petrifilm, you will want to to associate each sample with a short, abbreviated codename like “A1” or “TUR-3”.
1. When you are ready for inoculation, place the 3M petrifilm plate on a level surface. Use a permanent marker to label the corner of the petrifilm with the codename of the sample that it will be used for.
2. Shake the sample gently to make sure the bacteria are not at the top or bottom of the sample. With a sterile pipette, draw 1mL of samples from the chosen sample vial. (See Figure 2.
3. Lift the clear top film and with the pipette perpendicular to the inoculation area slowly dispense 1m L of s a m pl e s o nt o th e c en te r of t he b ot t om f i lm . (s ee F i g ur e 3. )

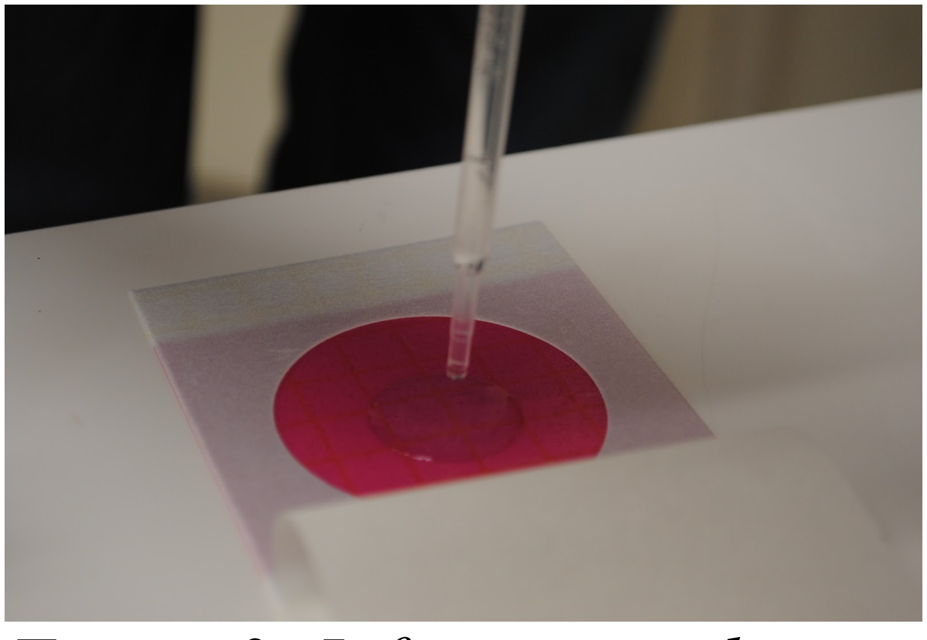
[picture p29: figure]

Figure 3: Lift cover and
dispense 1 ml
4. Carefully roll the top film down onto the sample to prevent trapping air bubbles. (see Figure 4.)

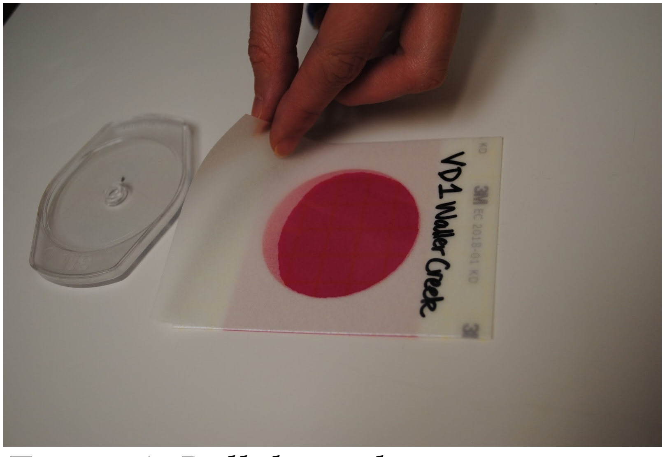
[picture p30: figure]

Figure 4: Roll down the cover
5. Place the 3M Petrifilm spreader with the flat side down on the center of the 3M Petrifillm plate. Press gently on the center of the 3M Petrifilm spreader to distribute the sample evenly. Do not slide the 3M Petrifilm Spreader across the film.
6. Remove the 3M Petrifilm spreader and leave the 3M Petrifilm plate undisturbed for at least one minute to permit the gel to form.
7. Your samples are ready to be placed in the Armadillo for incubation. Be sure to handle the Petrifilms carefully when transferring to the Armadillo.

8. You are allowed to stack as many 20 petrifilms together, but not more than that. The Armadillo allows you to incubate 40 petrifilms with a small cardboard stand for a second stack of 20.

For field work, the inexpensive, individually wrapped, sterile plastic 1ml transfer pipette and 5ml water vials are essential aids. They can be easily ordered by mail.
Samples should be inoculated in less than 24 hours after colleciton. Inoculation is as simple as dispensing 1 ml of the sample onto the petrifilm plate and ensuring that the sample is sealed cleanly on the film.

Incubation instructions
To Incubate, place a fully charged battery in the incubator, plug it in and turn it on.
Place the petrifilms in stacks of up to 20 on each of up to two cardboard shelves created from the provided templates. Screw the inner chamber lid down onto the gasket with the four provided screws and the small screwdriver.
Keep the Armadillo more or less upright. After an hour, check the analog thermometer that the temperature has risen to approximately 37C. This check is only to confirm that there is no loose connection or some other problem.
Remember to open the Armadillo in approximately 48 hours and proceed to post-incubation sample handling.

Post-Incubation Sample Handling
Incubated petrifilms are not completely stable, so after incubation, the films should be immediately photographed. Photographing them can be done conveniently with a cell phone with a camera. Care should be taken to have diffuse lighting so that glare does not obscure the labeling or growth medium of the petriflm. Petrifilms change their appearance slowly after incubation, so it is important to take photos immediately.
Once you safely have photos, we recommend you dispose of the Petrifilms as they are a slight biohazard.
The E. Coli colonies should be counted from the photographs and the counts carefully recorded, for example in a spreadsheet. Figure 5 shows the same petrifilm immediately after incubation and the 5 days later, demonstrating that the gas bubbles critical to the E. Coli colony identification degrade or migrate over time.

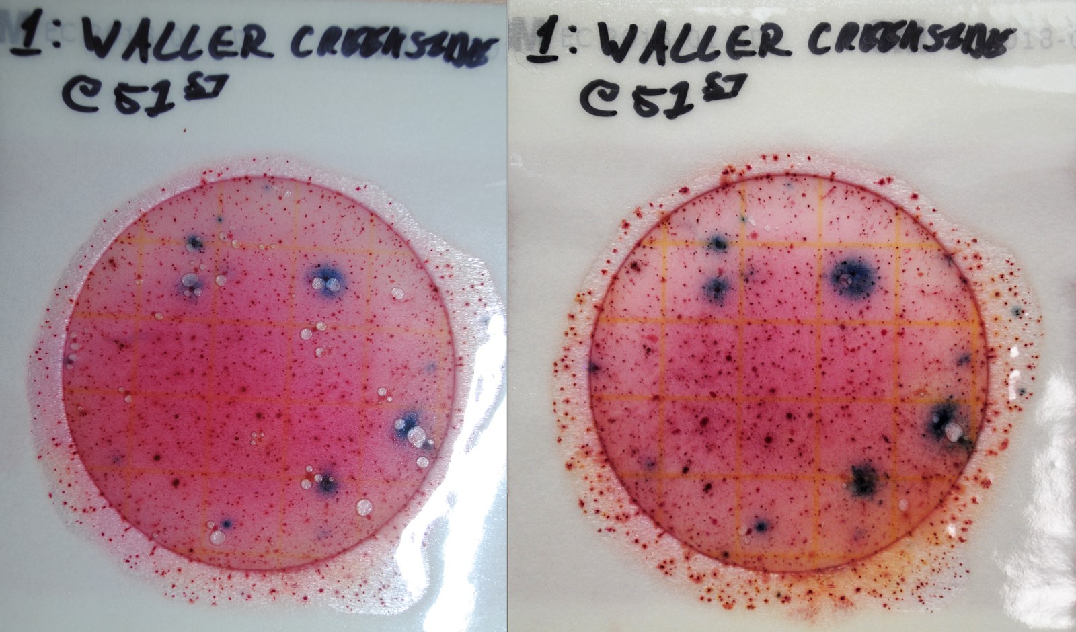
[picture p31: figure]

Figure 5: the same plate after 5 days of elapsed time

After incubation, ensure that the petrifilms stay outside of the inner chamber. Moisture from the petrifilms will condense on the inner surface of the chamber which might cause problems with future experiments.

Storage During Incubation instructions
The Armadillo should be stored upright and level in a location out of direct sunlight at a temperature less than body temperature. In general any place where a human being is comfortable will be warm enough to ensure a successful 48-hour incubation on a single battery charge. In temperatures near freezing the battery may not last 48-hours.

Field Use and Interpretation
One of the major advantages of portable Petrifilm incubation is that the incubated films provide visually striking and easy-to-understand results that can help the target community understand the clearly understand the problem. Numerical data returned from a distant laboratory may not have the same impact.

The Petrifilm approach allows comparison of different water sources. For example, one can clearly compare water run through a sand-filter, or UV-filter with unfiltered water. As is often pointed out, the mere presence of E. Coli does not directly indicate pathogenic organisms in water, but rather is a reliable indication of a sources of fecal contamination.

Limitations
Petrifilms are probably not useful when the water is either too clean or dirty. That is, some samples will produce “too many to count” colonies, or will generate no E. Coli colonies at all, as does sterile water and even tap water in the U.S.A. The WHO has recommended testing 100 ml of water, which is difficult to do with petriflims, which test 1 ml at a time.
The presence of E. Coli does not directly indicate pathogenic organisms or pathogenic E. Coli, but rather indicates fecal contamination, from human or non-human sources. Although this is an indirect measure of the the pathogenicity of the water, it is useful for comparing water sources and water treatments.

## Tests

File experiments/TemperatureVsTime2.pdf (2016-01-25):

Sheet1

00:05 | 15.91 | 00:05
00:10 | 15.23 | 00:05
00:15 | 16.86 | 00:05
00:20 | 17.49 | 00:05
00:25 | 18.49 | 00:05
00:30 | 19.74 | 00:05
00:35 | 21.93 | 00:05
00:40 | 22.43 | 00:05
00:45 | 23.55 | 00:05
00:50 | 23.43 | 00:05
00:55 | 25.18 | 00:05
01:00 | 25.05 | 00:05
01:05 | 26.92 | 00:05
01:10 | 26.3 | 00:05
01:15 | 27.92 | 00:05
01:20 | 27.05 | 00:05
01:25 | 28.05 | 00:05
01:30 | 28.05 | 00:05
01:35 | 29.17 | 00:05
01:40 | 29.67 | 00:05
01:45 | 29.8 | 00:05
01:50 | 29.8 | 00:05
01:55 | 30.3 | 00:05
02:00 | 30.67 | 00:05
02:05 | 31.8 | 00:05
02:10 | 31.3 | 00:05
02:15 | 32.29 | 00:05
02:20 | 32.54 | 00:05
02:25 | 32.92 | 00:05
02:30 | 33.54 | 00:05
02:35 | 33.42 | 00:05
02:40 | 32.67 | 00:05
02:45 | 33.79 | 00:05
02:50 | 33.92 | 00:05
02:55 | 34.42 | 00:05
03:00 | 34.04 | 00:05
03:05 | 34.67 | 00:05
03:10 | 34.17 | 00:05
03:15 | 34.67 | 00:05
03:20 | 34.92 | 00:05
03:25 | 35.42 | 00:05
03:30 | 35.29 | 00:05
03:35 | 36.17 | 00:05
03:40 | 34.92 | 00:05
03:45 | 39.04 | 00:05
03:50 | 37.41 | 00:05
03:55 | 36.67 | 00:05
04:00 | 32.17 | 00:05
04:05 | 32.79 | 00:05
04:10 | 33.29 | 00:05

Note: Battery lasted 15 hours, which is good, inability to stay in the teperature seems limited and jittery.

Page

2

04:15 | 33.67 | 00:05
04:20 | 33.79 | 00:05
04:25 | 34.42 | 00:05
04:30 | 33.92 | 00:05
04:35 | 34.54 | 00:05
04:40 | 34.29 | 00:05
04:45 | 38.79 | 00:05
04:50 | 37.91 | 00:05
04:55 | 36.67 | 00:05
05:00 | 32.42 | 00:05
05:05 | 32.54 | 00:05
05:10 | 32.79 | 00:05
05:15 | 33.29 | 00:05
05:20 | 33.54 | 00:05
05:25 | 34.42 | 00:05
05:30 | 34.04 | 00:05
05:35 | 35.04 | 00:05
05:40 | 35.17 | 00:05
05:45 | 35.29 | 00:05
05:50 | 34.54 | 00:05
05:55 | 39.04 | 00:05
06:00 | 38.16 | 00:05
06:05 | 37.04 | 00:05
06:10 | 32.42 | 00:05
06:15 | 32.42 | 00:05
06:20 | 32.79 | 00:05
06:25 | 33.79 | 00:05
06:30 | 33.67 | 00:05
06:35 | 34.67 | 00:05
06:40 | 34.17 | 00:05
06:45 | 34.54 | 00:05
06:50 | 34.67 | 00:05
06:55 | 35.92 | 00:05
07:00 | 34.92 | 00:05
07:05 | 35.79 | 00:05
07:10 | 35.17 | 00:05
07:15 | 38.66 | 00:05
07:20 | 37.41 | 00:05
07:25 | 36.42 | 00:05
07:30 | 31.55 | 00:05
07:35 | 32.17 | 00:05
07:40 | 33.55 | 00:05
07:45 | 33.42 | 00:05
07:50 | 33.79 | 00:05
07:55 | 34.54 | 00:05
08:00 | 34.92 | 00:05
08:05 | 35.29 | 00:05
08:10 | 35.04 | 00:05
08:15 | 35.42 | 00:05
08:20 | 34.54 | 00:05
08:25 | 39.04 | 00:05
08:30 | 38.04 | 00:05

Page

3

08:35 | 37.04 | 00:05
08:40 | 32.17 | 00:05
08:45 | 32.67 | 00:05
08:50 | 32.67 | 00:05
08:55 | 33.67 | 00:05
09:00 | 33.17 | 00:05
09:05 | 33.54 | 00:05
09:10 | 33.67 | 00:05
09:15 | 35.17 | 00:05
09:20 | 34.17 | 00:05
09:25 | 36.04 | 00:05
09:30 | 35.17 | 00:05
09:35 | 39.16 | 00:05
09:40 | 38.04 | 00:05
09:45 | 37.04 | 00:05
09:50 | 36.04 | 00:05
09:55 | 32.54 | 00:05
10:00 | 32.67 | 00:05
10:05 | 33.79 | 00:05
10:10 | 33.42 | 00:05
10:15 | 34.54 | 00:05
10:20 | 34.17 | 00:05
10:25 | 34.54 | 00:05
10:30 | 33.92 | 00:05
10:35 | 35.54 | 00:05
10:40 | 34.67 | 00:05
10:45 | 38.16 | 00:05
10:50 | 37.04 | 00:05
10:55 | 36.17 | 00:05
11:00 | 32.17 | 00:05
11:05 | 33.17 | 00:05
11:10 | 32.92 | 00:05
11:15 | 33.67 | 00:05
11:20 | 33.54 | 00:05
11:25 | 34.67 | 00:05
11:30 | 33.67 | 00:05
11:35 | 35.17 | 00:05
11:40 | 34.04 | 00:05
11:45 | 34.67 | 00:05
11:50 | 34.92 | 00:05
11:55 | 38.91 | 00:05
12:00 | 37.41 | 00:05
12:05 | 36.67 | 00:05
12:10 | 31.55 | 00:05
12:15 | 32.67 | 00:05
12:20 | 33.17 | 00:05
12:25 | 33.79 | 00:05
12:30 | 33.67 | 00:05
12:35 | 34.29 | 00:05
12:40 | 34.42 | 00:05
12:45 | 35.17 | 00:05
12:50 | 34.79 | 00:05

12:55 | 35.17 | 00:05
13:00 | 35.04 | 00:05
13:05 | 35.04 | 00:05
13:10 | 34.54 | 00:05
13:15 | 34.79 | 00:05
13:20 | 35.04 | 00:05
13:25 | 38.41 | 00:05
13:30 | 37.04 | 00:05
13:35 | 36.17 | 00:05
13:40 | 32.04 | 00:05
13:45 | 32.92 | 00:05
13:50 | 32.79 | 00:05
13:55 | 33.42 | 00:05
14:00 | 33.29 | 00:05
14:05 | 33.79 | 00:05
14:10 | 33.42 | 00:05
14:15 | 34.17 | 00:05
14:20 | 33.79 | 00:05
14:25 | 34.29 | 00:05
14:30 | 34.04 | 00:05
14:35 | 34.29 | 00:05
14:40 | 33.79 | 00:05
14:45 | 34.42 | 00:05
14:50 | 36.67 | 00:05
14:55 | 32.04 | 00:05
15:00 | 31.17 | 00:05

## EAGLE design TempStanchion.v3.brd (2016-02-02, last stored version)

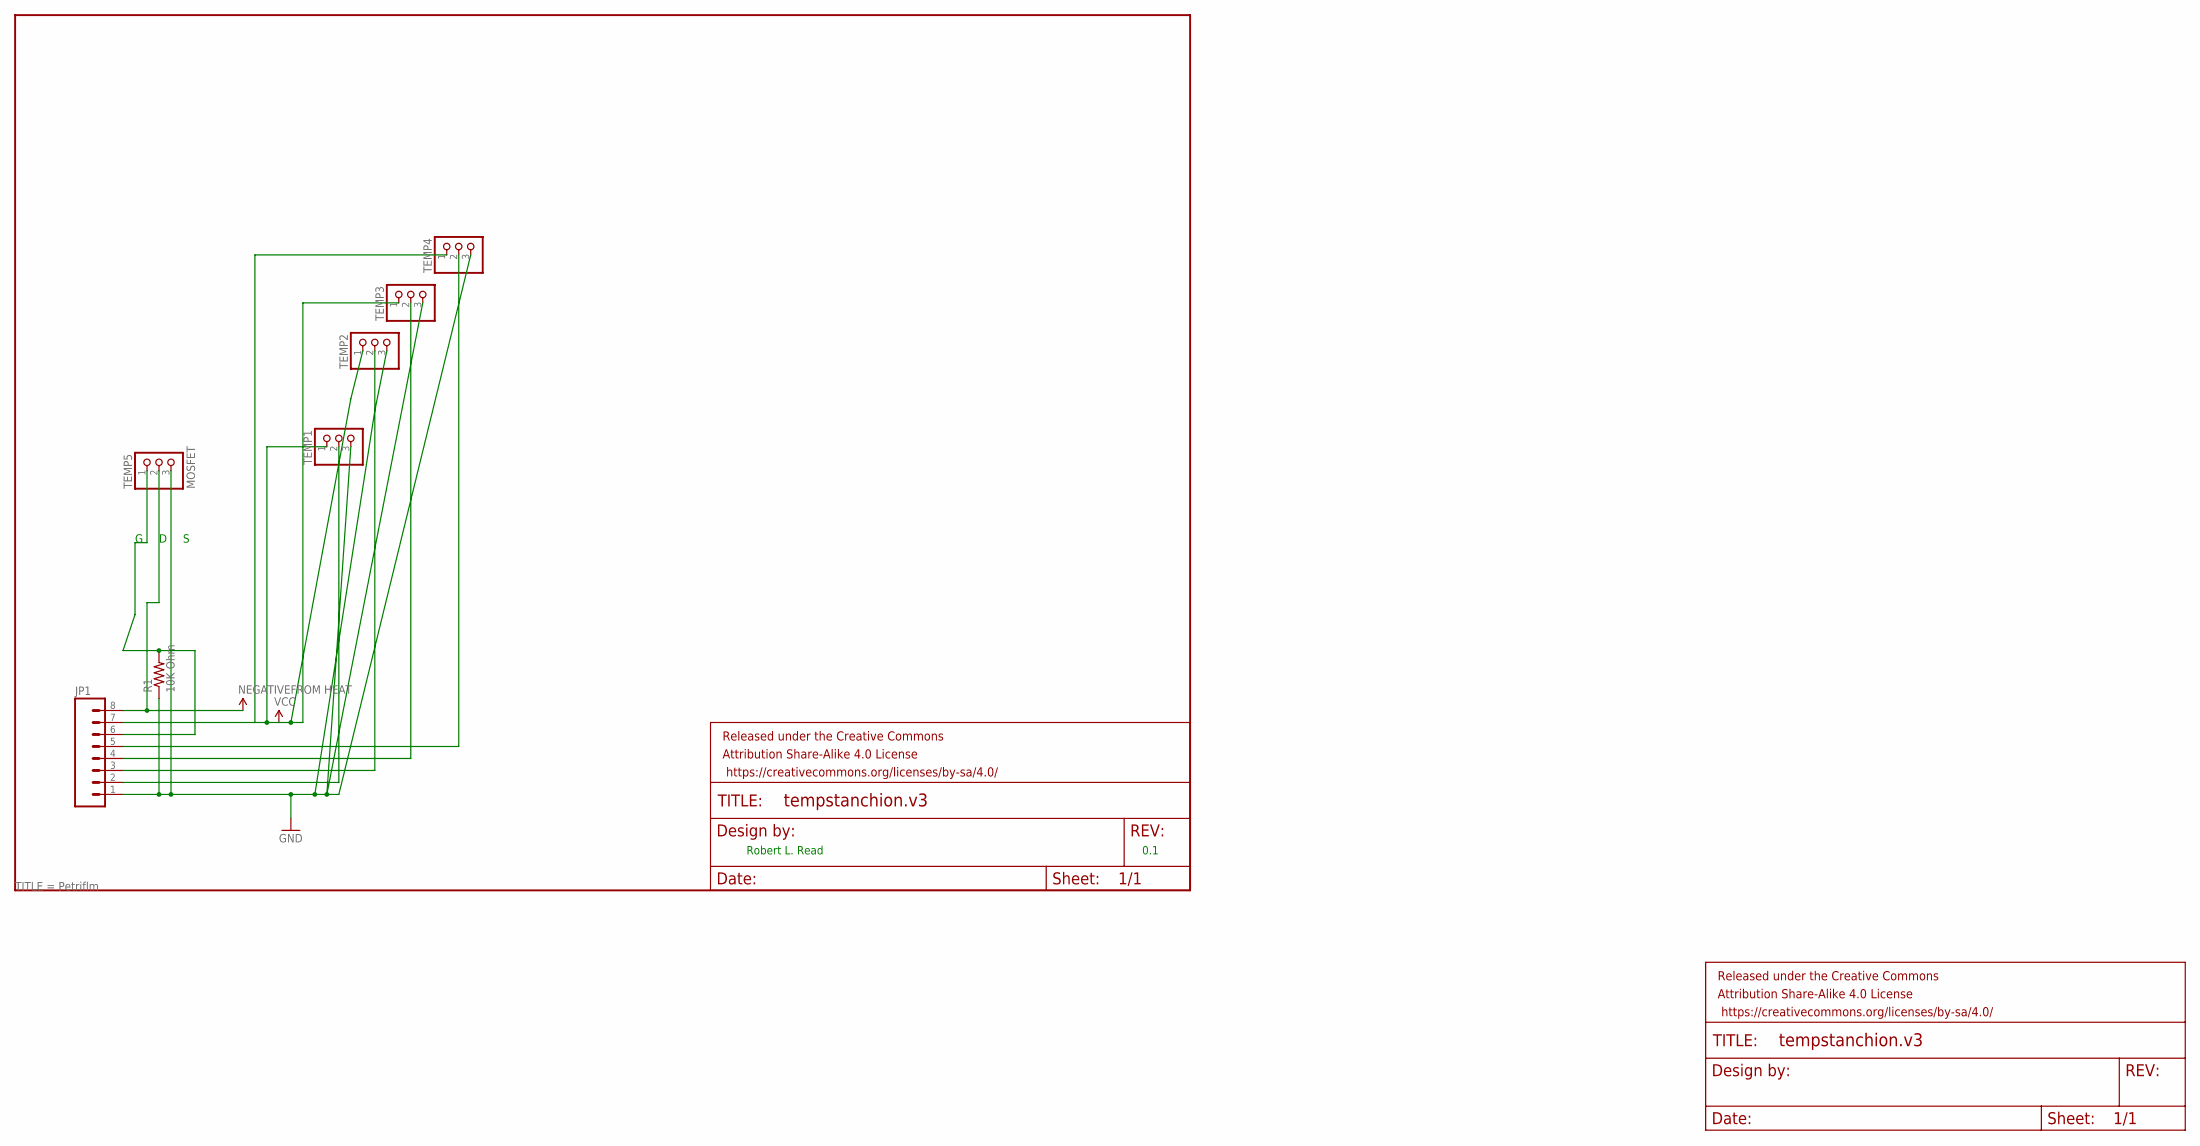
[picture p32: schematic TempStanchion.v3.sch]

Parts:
FRAME1, FRAME2: FRAME-LETTER; CREATIVE_COMMONS
JP1: M08; 1X08_ROUND
R1: 10K Ohm; AXIAL-0.6
TEMP1, TEMP2, TEMP3, TEMP4: PINHD-1X3; 1X03
TEMP5: MOSFET; 1X03

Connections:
GND: JP1.1, R1.P$1 (1), TEMP1.3, TEMP2.3, TEMP3.3, TEMP4.3, TEMP5.3
MOSFET: JP1.6, R1.P$2 (2), TEMP5.1
unnamed: JP1.2, TEMP1.2
unnamed: JP1.3, TEMP2.2
unnamed: JP1.4, TEMP3.2
unnamed: JP1.5, TEMP4.2
VCC: JP1.7, JP1.8, TEMP1.1, TEMP2.1, TEMP3.1, TEMP4.1, TEMP5.2

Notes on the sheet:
Robert L. Read
0.1

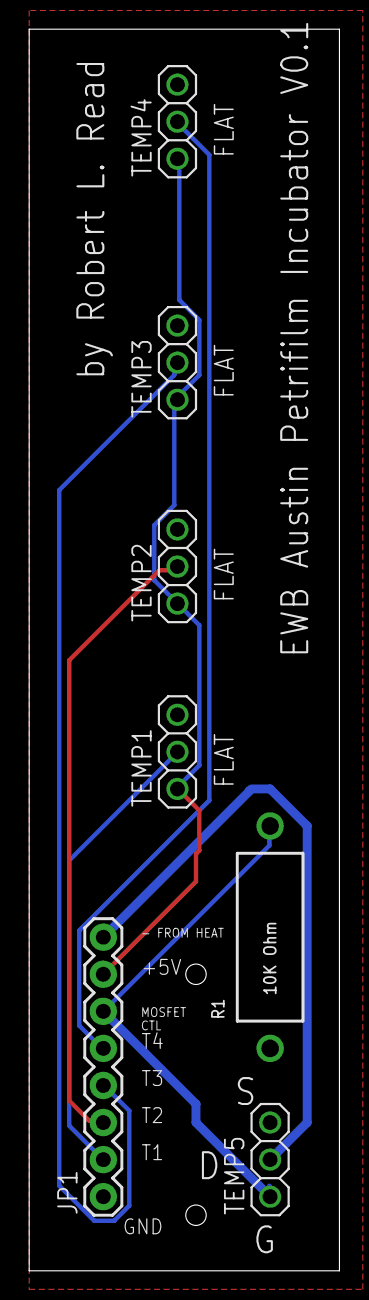
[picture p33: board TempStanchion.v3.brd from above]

Board: 2 copper layers, 21.3 x 85.1 mm, 9 parts (0 on the bottom side), 7 nets.

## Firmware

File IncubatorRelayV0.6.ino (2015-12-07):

// Copyright Robert L. Read, <read.robert@gmail.com>, Andrew Wong, Ryan Syed, and Michelle Tate.

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
#include <EEPROM.h>

#include <TimerOne.h>

#include <stdint.h>  // CAN ARDUINO USE STDINT.h?


#include <LiquidCrystal.h>
#include <Keypad.h>

//Pin assignments for DFRobot LCD Keypad Shield
LiquidCrystal lcd(8, 9, 4, 5, 6, 7); 
//---------------------------------------------
// Keypad keypad;


 const float MAX_TEMP = 38.0;  //normally 38.0
 const float MIN_TEMP = 34.0;
 const float ALARM_MAX = 37.0;
 const float ALARM_MIN = 20.0; //very low for testing
 
 const int MOSFET_PIN = 3; 
 const int ALARM_PIN = 7;
 
 const int DEBUG_LEVEL = 1;
 
int ledDigitalOne[] = {9, 10, 11}; //the three digital pins of the digital LED 
                                   //9 = redPin, 10 = greenPin, 11 = bluePin

const boolean ON = LOW;     //Define on as LOW (this is because we use a common 
                            //Anode RGB LED (common pin is connected to +5 volts)
const boolean OFF = HIGH;   //Define off as HIGH

//TMP36 Pin Variables
// int temperaturePin = 0; //the analog pin the TMP36's Vout (sense) pin is connected to
                        //the resolution is 10 mV / degree centigrade 
                        //(500 mV offset) to make negative temperatures an option
                        
int speakerPin = 7;

int length = 4; // high notes for high-temp alarm, low notes for low-temp alarm
char highnotes[] = "cga "; 
int beats[] = { 1, 1, 2, 1};

char lownotes[] = "bac "; 

int tempo = 300;

void playTone(int tone, int duration) {
  for (long i = 0; i < duration * 1000L; i += tone * 2) {
    digitalWrite(speakerPin, HIGH);
    delayMicroseconds(tone);
    digitalWrite(speakerPin, LOW);
    delayMicroseconds(tone);
  }
}


void playNote(char note, int duration) {
  char names[] = { 'c', 'd', 'e', 'f', 'g', 'a', 'b', 'C' };
  int tones[] = { 1915, 1700, 1519, 1432, 1275, 1136, 1014, 956 };
  
  // play the tone corresponding to the note name
  for (int i = 0; i < 8; i++) {
    if (names[i] == note) {
      playTone(tones[i], duration);
    }
  }
}

                        
void sound_hot_alarm()
{
       if (DEBUG_LEVEL > 0) 
         Serial.println("Temperature WAY Too Hot, ALARMING_HOT!"); 
       for (int i = 0; i < length; i++) {
         if (highnotes[i] == ' ') {
           delay(beats[i] * tempo);
         } else {
           playNote(highnotes[i], beats[i] * tempo);
         }
       }
}

void sound_cold_alarm()
{
        if (DEBUG_LEVEL > 0) 
          Serial.println("Temperature WAY Too Cool, ALARMING_COLD!"); 
        for (int i = 0; i < length; i++) {
         if (highnotes[i] == ' ') {
           delay(beats[i] * tempo);
         } else {
           playNote(lownotes[i], beats[i] * tempo);
         }
       };
}
                        
void alarm_if_needed(float temp) {
     if (temp < ALARM_MIN) {
     sound_cold_alarm();
   } else if (temp > ALARM_MAX) {
     sound_hot_alarm();
   }
}

void process_input() {
  if (Serial.available()) {
    bool terminator_not_found = true;
    char inChar = Serial.read();
    Serial.println(inChar);
    if (inChar == 'd') {
      Serial.println("dumping");
      print_dump();
    }
    
    if (inChar == 'x') {
          Serial.println("clearing");
      clear_EEPROM();
    }
    

      char terminator = Serial.read();
      if (terminator != '\n') {
        Serial.print(terminator);
        Serial.println(" : Didn't read terminator successfully.");
      }
  }
}

float get_average_temperature(long vcc) {
   float t5 = getVoltage(A5,vcc); 
   float tc5 = (t5 - .5) * 100.0; 
   float t4 = getVoltage(A4,vcc); 
   float tc4 = (t4 - .5) * 100.0; 
   float t3 = getVoltage(A3,vcc); 
   float tc3 = (t3 - .5) * 100.0;    
   float t2 = getVoltage(A2,vcc); 
   float tc2 = (t2 - .5) * 100.0;
   Serial.print("t5 = ");
   Serial.println(t5);
   Serial.println(tc5);
   int rawRead;
   rawRead = analogRead(A5);
   Serial.println(rawRead);
   Serial.print("t4 = ");
   Serial.println(t4);
   Serial.println(tc4);
   rawRead = analogRead(A4);
   Serial.println(rawRead);
   Serial.print("t3 = ");
   Serial.println(t3);
   Serial.println(tc3);
   rawRead = analogRead(A3);
   Serial.println(rawRead);
   Serial.print("t2 = ");
   Serial.println(t2);
   Serial.println(tc2);
   rawRead = analogRead(A2);
   Serial.println(rawRead);

          
   float avg = (tc2+tc3+tc4+tc5)/ 4.0;
   return avg;
                                                  
}
 
void loop()                     // run over and over again
{
 Serial.println("VCC = ");
  long vcc = readVcc();
   Serial.println(vcc);
   lcd.clear();
 lcd.setCursor(0, 0);
 lcd.print("VCC: ");
 lcd.print(vcc);
 delay(2000);
  
  process_input();
  
 float temperature = getVoltage(A5,vcc);  //getting the voltage reading from the temperature sensor
 temperature = (temperature - .5) * 100;          //converting from 10 mv per degree wit 500 mV offset
                                                  //to degrees ((volatge - 500mV) times 100)
 int rawRead = analogRead(A5);
// Serial.println(rawRead);
 
temperature = get_average_temperature(vcc);
 Serial.print("temp:");
 Serial.println(temperature);                     //printing the result


 // print to LCD screen
 lcd.clear();
 lcd.setCursor(0, 0);
 lcd.print("Temp: ");
 lcd.print (temperature);
   if (temperature < MIN_TEMP) {
       if (DEBUG_LEVEL > 0) 
         Serial.println("Temperature Too Cool, turning On!"); 
         lcd.setCursor(0,1);
         lcd.print("2 Cool - Pad ON");
     digitalWrite(MOSFET_PIN, LOW);
//     turn_MOSFET_ON(100.0);
   } else if (temperature > MAX_TEMP) {
       if (DEBUG_LEVEL > 0) 
         Serial.println("Temperature Too Hot, turning Off!"); 
         lcd.setCursor(0,1);
         lcd.print("2 Hot - Pad OFF");
     digitalWrite(MOSFET_PIN, HIGH);
//     turn_MOSFET_ON(0.0);

   } else {
     // do nothing!
     if (DEBUG_LEVEL > 0) 
         Serial.println("Temperature OK, turning Off!"); 
        digitalWrite(MOSFET_PIN, HIGH);
   }
   alarm_if_needed(temperature);
   
 //  record_temp(temperature);
   delay(5000);
}

void turn_MOSFET_ON(float percent){
  int pwm = (percent * 256) / 100;
  pwm = (pwm > 255) ? 255 : pwm;
  if (DEBUG_LEVEL > 0) 
    Serial.println(pwm);
  analogWrite(MOSFET_PIN, pwm);
}

long readVcc() {
  // Read 1.1V reference against AVcc
  // set the reference to Vcc and the measurement to the internal 1.1V reference
  #if defined(__AVR_ATmega32U4__) || defined(__AVR_ATmega1280__) || defined(__AVR_ATmega2560__)
    ADMUX = _BV(REFS0) | _BV(MUX4) | _BV(MUX3) | _BV(MUX2) | _BV(MUX1);
  #elif defined (__AVR_ATtiny24__) || defined(__AVR_ATtiny44__) || defined(__AVR_ATtiny84__)
    ADMUX = _BV(MUX5) | _BV(MUX0);
  #elif defined (__AVR_ATtiny25__) || defined(__AVR_ATtiny45__) || defined(__AVR_ATtiny85__)
    ADMUX = _BV(MUX3) | _BV(MUX2);
  #else
    ADMUX = _BV(REFS0) | _BV(MUX3) | _BV(MUX2) | _BV(MUX1);
  #endif  

  delay(2); // Wait for Vref to settle
  ADCSRA |= _BV(ADSC); // Start conversion
  while (bit_is_set(ADCSRA,ADSC)); // measuring

  uint8_t low  = ADCL; // must read ADCL first - it then locks ADCH  
  uint8_t high = ADCH; // unlocks both

  long result = (high<<8) | low;

  result = 1125300L / result; // Calculate Vcc (in mV); 1125300 = 1.1*1023*1000
  return result; // Vcc in millivolts
}

// this code copied from ARDX (thanks!)

/*
 * getVoltage() - returns the voltage in millivutoes.on the analog input defined by
 * pin
 */
float getVoltage(int pin, long vcc){
 int v = analogRead(pin);
 if (DEBUG_LEVEL > 0) {
   Serial.println("input voltage");
   Serial.println(v);
 }
 return (v * (vcc / 1000.0) / 1024.0); //converting from a 0 to 1023 digital range
                                        // to 0 to 5 volts (each 1 reading equals ~ 5 millivolts
}

void setup(){
  lcd.begin(16, 2);
  lcd.clear();
  lcd.setCursor(0, 0);
  lcd.print("Inc Relay V0.5");
  delay(1500);
  pinMode(MOSFET_PIN,OUTPUT);
  pinMode(speakerPin, OUTPUT);
  pinMode(A5,INPUT);
  pinMode(A4,INPUT);
  pinMode(A3,INPUT);
  pinMode(A2,INPUT);
  

  Serial.begin(9600);  //Start the serial connection with the copmuter
                       //to view the result open the serial monitor 
                       //last button beneath the file bar (looks like a box with an antenae)
                       
 // setup_interrupt();
                       
}

const int LED = 13;

// ========================EEPROM DATA DUMP FUNCTIONS==========================
// Authors: Andrew Wong, Ryan Syed, Michelle Tate
// Stores number of data entries in bytes 0 - 1 (needs 10 bits to address 1021 bytes), and temperature data in entries 2 - 1023
// Timer 1 library can be downloaded from: http://www.pjrc.com/teensy/td_libs_TimerOne.html






int numData = 0;  // number of data entries in EEPROM
int dataAddr = sizeof(numData); 
int time_5s = 0;
// <global temperature variable definition goes here>
int ledState = LOW;

volatile unsigned long blinkCount = 0; // use volatile for shared variables


 // print out EEPROM contents
void print_dump(){
  int i = 0;
  float data = 0.0;
  int numSamples = 0;  // store number of entries in address 0 - 1 (big endian)
  numSamples = EEPROM.get(0,numSamples);
  Serial.print("numSamples = ");
  Serial.println(numSamples);
  while (i < numSamples) {
    EEPROM.get(sizeof(int) + i * sizeof(float),data);
    Serial.print(" i = ");
    Serial.println(i);
    Serial.print(data);
    i++;
  } 
}



void clear_EEPROM(){
  numData = 0;
  EEPROM.put(0,numData);

    // turn the LED on when we're done
  digitalWrite(13, HIGH);

}





 // test interrupt
void blinkLED(void)
{
  if (ledState == LOW) {
    ledState = HIGH;
    blinkCount = blinkCount + 1;  // increase when LED turns on
  } else {
    ledState = LOW;
  }

  digitalWrite(LED, ledState);
}





 // writes 1 byte of data to EEPROM every 360 x 5s = 30 minutes
 // toggles LED to indicate write finished 
 // Note: maximum time betw Timer1 interrupts is 8.3s
void data_dump(){
    Serial.println("RECORD_DATA");
  if (time_5s >= 2){
    
    // Let's get the temp...
     long vcc = readVcc();
    float temperature = get_average_temperature(vcc);
     // store number of entries in address 0x0 - 0x1 
    record_temp(temperature);
     time_5s = 0;
  }
  else{
    time_5s++;
  }
}
  
void record_temp(float temperature) {


     // most sig byte in 0x0, least sig byte in 0x1 (big endian)
//    uint8_t numD_LSB = 0;
//    uint8_t numD_MSB = 0;
//    numD_LSB = numData & 0x00FF;  // mask upper 8 bits
//    numD_MSB = numData & 0xFF00;  // mask lower 8 bits
//    EEPROM.write(0, numD_MSB);
//    EEPROM.write(1, numD_LSB);

        numData++;
    EEPROM.put(0,numData);

    dataAddr = sizeof(int) + numData * sizeof(float);
    
     // store data
    EEPROM.put(dataAddr, temperature);   //NOTE: tempData is a global variable that is the temp measurement

    
     // toggle LED to indicate write is done

    if (ledState == LOW) {
      ledState = HIGH;
      //blinkCount = blinkCount + 1;  // increase when LED turns on
    } else {
      ledState = LOW;
    }

    digitalWrite(LED, ledState);
    // This is a little weird....
 
}

void setup_interrupt() {
  Timer1.initialize(5000000);  // interrupt every 5 seconds
  Timer1.attachInterrupt(data_dump); // array dump to run every 5 seconds
  Serial.begin(9600);
  pinMode(13, OUTPUT);    // initialize the LED pin as an output.
}

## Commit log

2015-12-30 Adding first experiment
    [TemperatureVsTime1.csv]
2016-01-25 Adding next experiment
    [TemperatureVsTime2.csv]
2016-02-02 adding Eagle files for board
    [TempStanchion.v3.brd, TempStanchion.v3.sch]
2016-02-12 full experiment
    [TemperateVsTimeFull.csv]
2017-02-21 create experiments directory
    [TemperateVsTimeFull.csv, TemperatureVsTime1.csv, TemperatureVsTime2.csv]
2017-02-28 removing files
    [TempStanchion.v3.brd, TempStanchion.v3.sch]
2017-03-21 Add files via upload
    Adding materials list and updating inoculation instructions

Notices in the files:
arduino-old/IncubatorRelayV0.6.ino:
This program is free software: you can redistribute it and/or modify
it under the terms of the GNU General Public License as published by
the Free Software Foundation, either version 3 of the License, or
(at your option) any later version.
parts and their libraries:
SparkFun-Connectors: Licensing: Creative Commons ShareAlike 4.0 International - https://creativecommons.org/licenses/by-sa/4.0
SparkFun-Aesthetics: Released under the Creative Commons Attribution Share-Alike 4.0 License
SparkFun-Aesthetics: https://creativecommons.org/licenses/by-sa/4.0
